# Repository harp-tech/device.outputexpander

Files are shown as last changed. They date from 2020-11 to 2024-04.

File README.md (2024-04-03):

## Harp Output Expander
Harp board to expand the outputs of the current harp ecosystem.

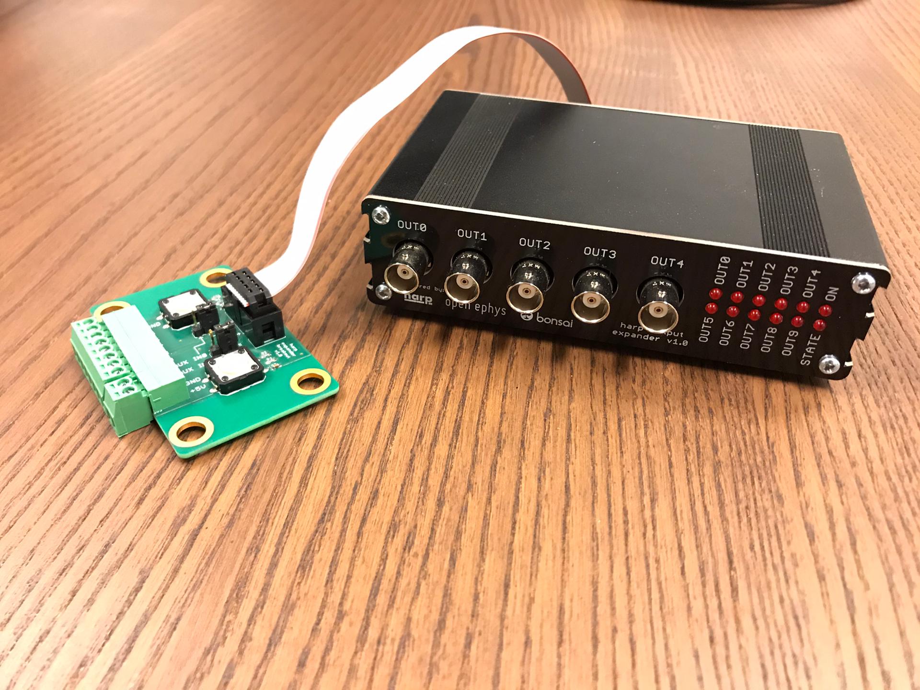
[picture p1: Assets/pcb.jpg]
HarpExpander


### Key Features ###

* TBA

### Connectivity ###

* TBA

## Interface ##

The interface with the Harp Output Expander can be done through [Bonsai](https://bonsai-rx.org/).

## Licensing ##

Each subdirectory will contain a license or, possibly, a set of licenses if it involves both hardware and software.

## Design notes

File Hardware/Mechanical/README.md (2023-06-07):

# Harp Expander Panels

## Licensing

The designs, documentation, and photos available in this repository are free: you can redistribute it and/or modify it under the terms of the used license.
Check file named LICENSE.

Copyright Filipe Carvalho 2020-2023

<br />This work is licensed under a <a rel="license" href="http://creativecommons.org/licenses/by-nc-sa/3.0/igo/">Creative Commons Attribution-NonCommercial-ShareAlike 3.0 IGO License</a>.

If your are interested in obtaining a license to sell this device, please contact info@oeps.tech

[1]: https://docs.google.com/spreadsheets/d/1aobmmEzBDethzIlrm1eg0eYkBqlyX3s9WbA9KgRwVQI/edit?usp=sharing

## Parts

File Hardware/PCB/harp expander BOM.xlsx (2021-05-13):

Qty | Value | Package | Parts | MPN | Type
PCB COMPONENTS
5 | BNC plug |  | BNC0, BNC1, BNC2, BNC3, BNC4 | 73100-0105 | TH
27 | 100nF | C0402 | C1, C3, C5, C7, C9, C12, C13, C14, C15, C16, C17, C18, C19, C20, C21, C22, C25, C26, C27, C28, C29, C30, C31, C32, C35, C36, C40 | MC0402B104K160CT | SMD
9 | 4.7uF | C0603 | C10, C11, C23, C24, C33, C34, C37, C38, C52 | C1608X6S1C475K080AC | SMD
1 | 4.7nF | C0402 | C2 | 885012205084 | SMD
1 | 100u 25V | TT2D6 | C39 | EEUFM1E101B | TH
2 | 47pF | C0402 | C4, C6 | 04025A470JAT2A | SMD
11 | 330pF | C0402 | C41, C42, C43, C44, C45, C46, C47, C48, C49, C50, C51 | C0402C331J5GACTU | SMD
2 | CLCK_JACK | 35RASMT2BHNTRX | CLKIN, CLKOUT | 35RASMT2BHNTRX | SMD
1 | XMEGA-A1TQFP | TQFP100 | IC1 | ATXMEGA128A1U-AU | SMD
1 | USBLC6-2SC6 | SOT23-6L | IC2 | USBLC6-2SC6 | SMD
1 | FT232RL | SSOP28 | IC3 | FT232RL-REEL | SMD
2 | TLV70033DDCR | TSOT23-5 | IC4, IC5 | TLV70033DDCR | SMD
1 | SI8610BC-B-IS | SO-08 | IC6 | SI8610EC-B-IS | SMD
4 | SN74LVC1G125DBVT | SOT23-5 | IC7, IC8, IC9, IC10 | SN74LVC1G125DBVT | SMD
1 | 40R@100MHz | R0805 | L1 | MI0805K400R-10 | SMD
6 | RED_LEDs | 569-011X-X00_LED_ARRAY | LED0, LED1, LED2, LED3, LED4, LED5 | 5690-111-100F | TH
1 | Oscillator | OSCILLATOR_3.2X2.5 | OSC | O 32,0-JT32C-A-K-3,3-LF | SMD | Alternative: DSC1001CI5-032.0000T
1 | PROG HEADER | MA03-2 | PDI | 67996-206HLF | TH
1 | 10R | R0402 | R2 | CRCW040210R0FKEDHP | SMD
12 | 1k | R0402 | R20, R21, R22, R23, R24, R25, R26, R27, R28, R29, R30, R31 | CRCW04021K00FKED | SMD
31 | 10k | R0402 | R3, R9, R10, R11, R12, R13, R14, R15, R16, R17, R19, R38, R43, R46, R47, R53, R54, R55, R56, R57, R58, R59, R60, R61, R62, R63, R64, R65, R66, R67, R68 | CRCW040210K0FKED | SMD
12 | 330R | R0402 | R32, R33, R34, R35, R36, R37, R39, R40, R41, R42, R44, R45 | RC0402FR-07330RL | SMD
11 | 100R | R0603 | R4, R5, R6, R7, R8, R48, R49, R50, R51, R52, R69 | CRCW0603100RFKEAHP | SMD
1 | I/O Header | ML10L | SV1 | SBH11-PBPC-D05-RA-BK | TH
12 | BC850 | SOT23 | T2, T3, T4, T5, T6, T7, T8, T9, T10, T11, T12, T13 | BC850C,215 | SMD
2 | 744245X | SO24L | U1, U2 | 74LVC4245AD,118 | SMD
1 | 74HCT125SO14 | SO14 | U3 | 74HCT125D,653 | SMD
1 | mini USB | 240-0002-1 | USB | UX60-MB-5S8 | SMD
1 |  |  | PCB
POST-PRODUCTION
1 |  |  | Front Panel PCB | PCBWAY
1 |  |  | Rear Panel PCB | PCBWAY
1 |  |  | Enclosure | B5-080BK
4 |  |  | Bumper Cylindrical Dome 9.53mm | SJ-5306-CLEAR-3000/CASE
ACCESSORIES
1 |  |  | 3.5mm stereo jack cable 1.2 m, Black | AV13646
1 |  |  | 0.9 left angle USB cable | USB2HABM3RA
NOTES
 |  |  |  | Number of unique parts | 28
 |  |  |  | Number of unique SMD parts | 23
 |  |  |  | Number of unique TH parts | 5
 |  |  |  | Number of SMD parts | 147
 |  |  |  | Number of TH parts | 14
 |  | Optional
 |  | Holder: MF80BK2

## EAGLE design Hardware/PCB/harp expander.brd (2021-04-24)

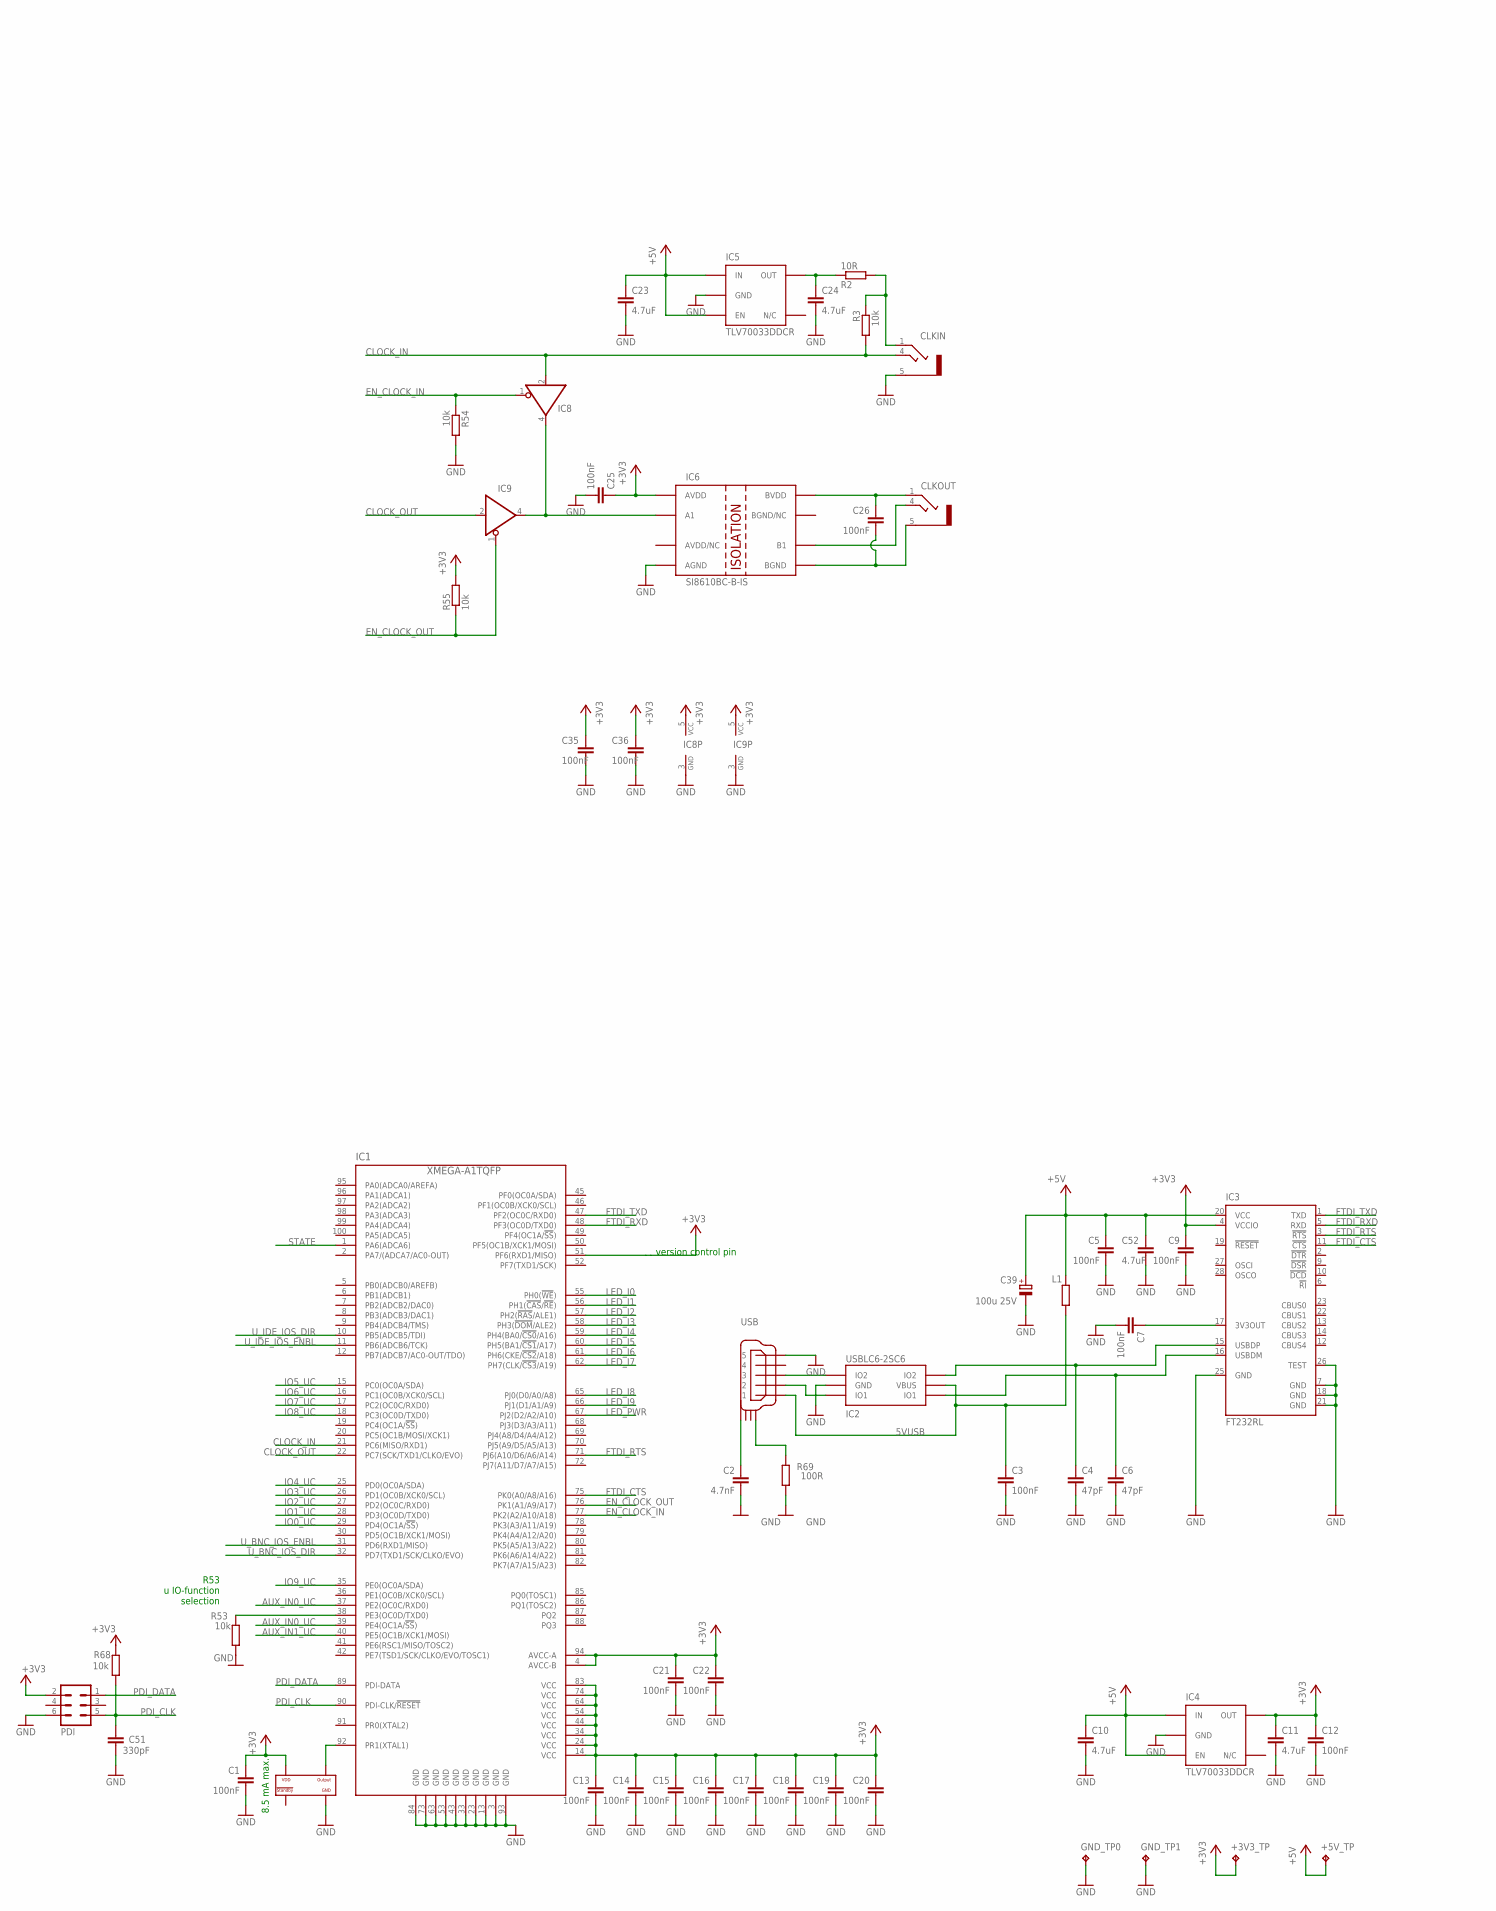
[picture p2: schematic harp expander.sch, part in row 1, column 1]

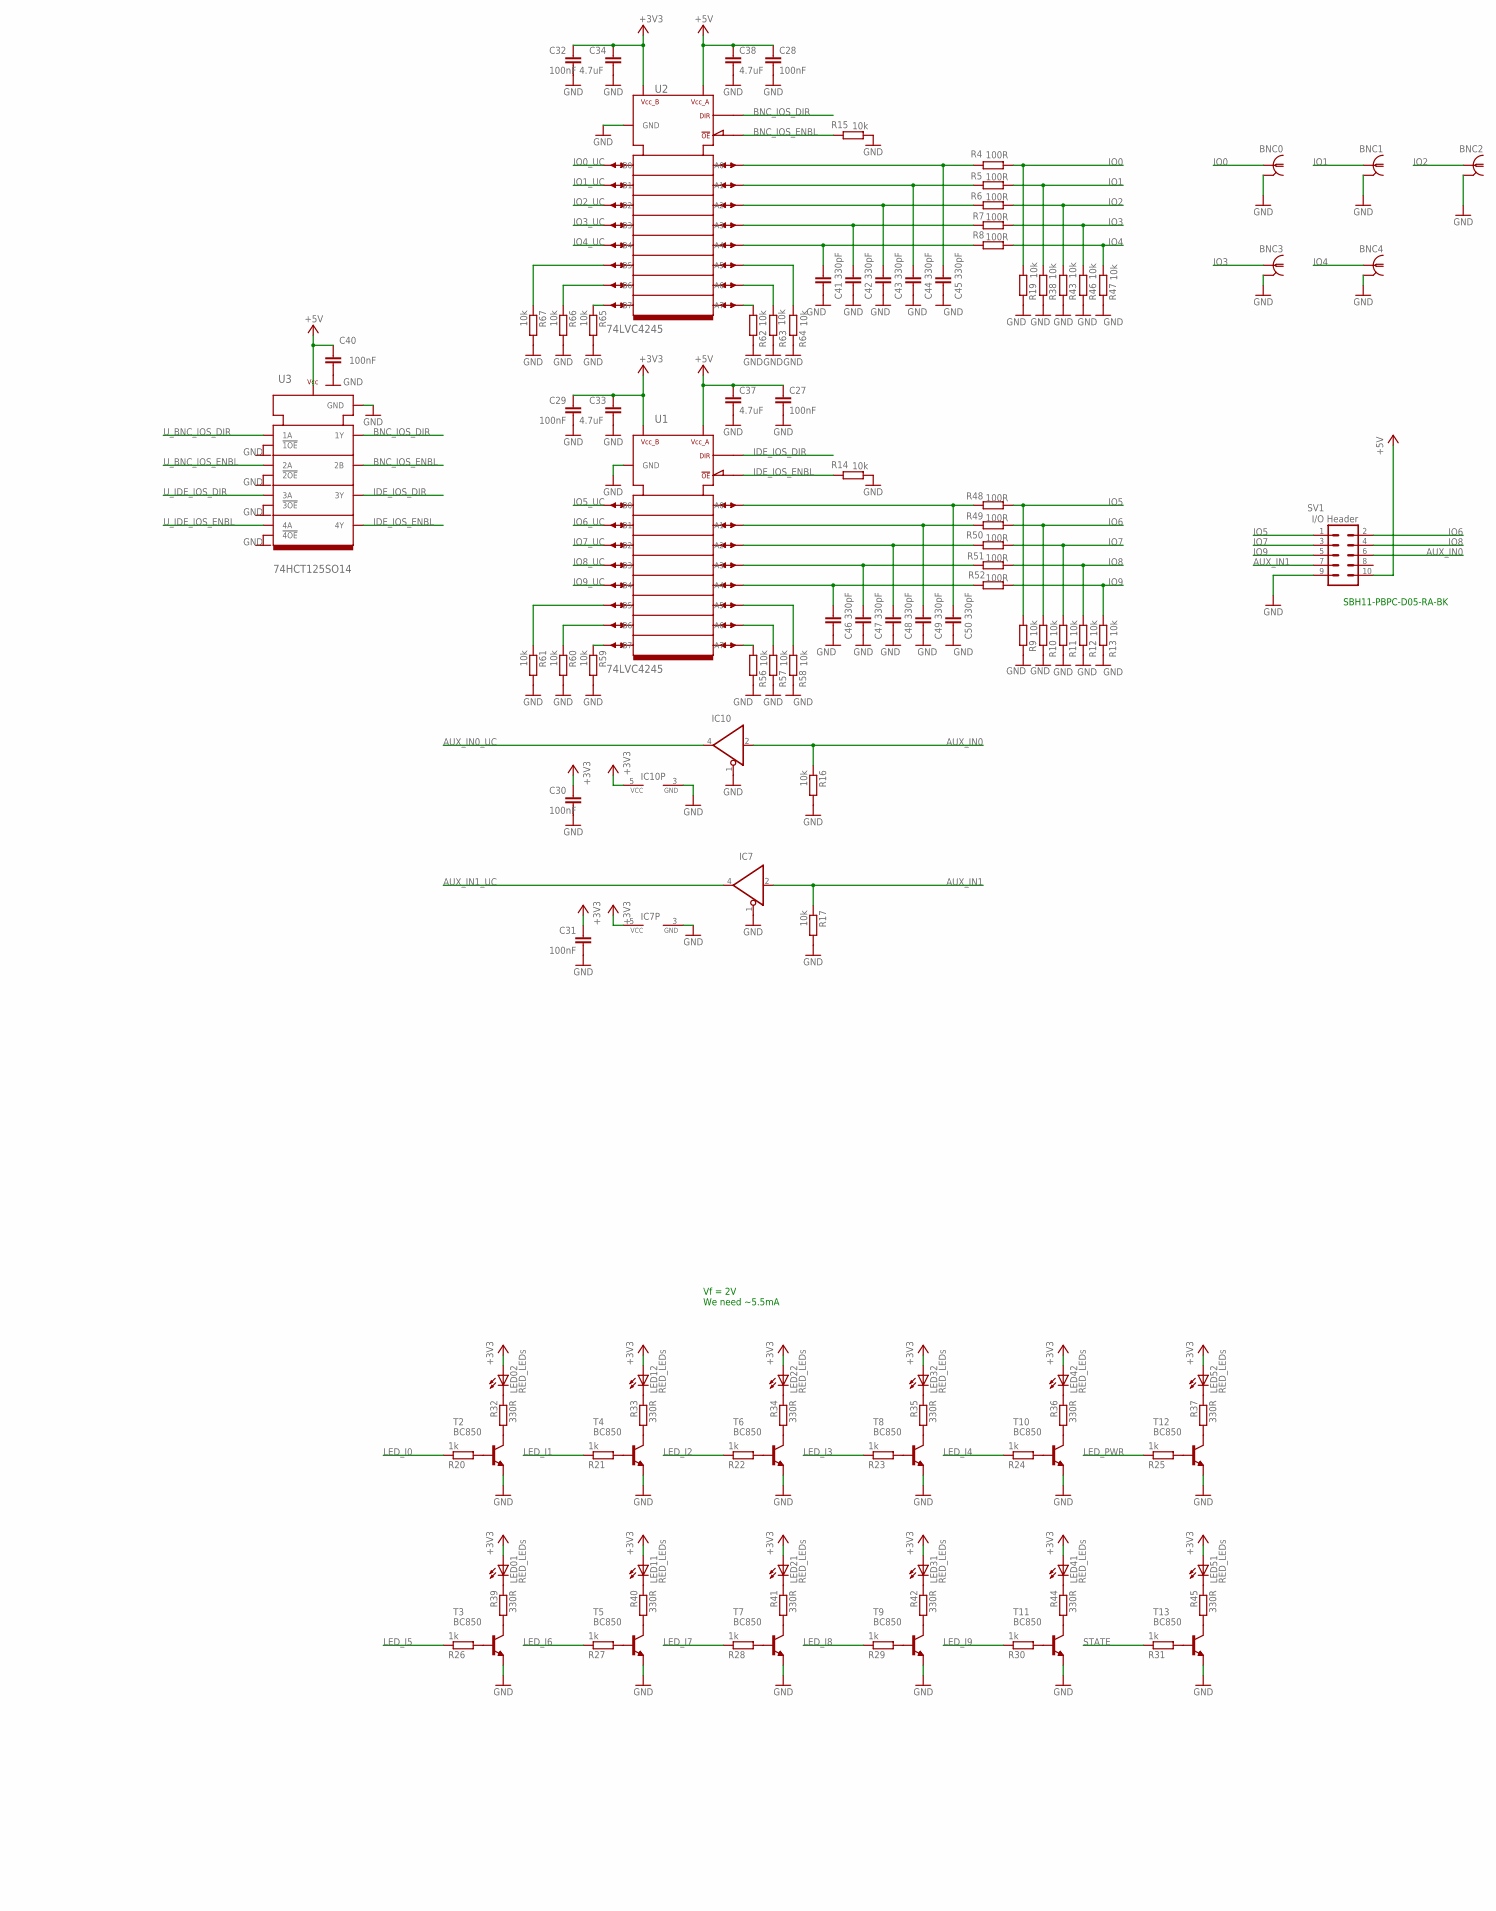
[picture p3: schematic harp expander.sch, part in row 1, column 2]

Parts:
+3V3_TP, +5V_TP: TPPAD1-13; P1-13; MPN n.a.
BNC0, BNC1, BNC2, BNC3, BNC4: BNC plug; 0731000105; MPN 73100-0105
C1, C3, C5, C7, C9, C12, C13, C14, C15, C16, C17, C18, C19, C20, C21, C22, C25, C26, C27, C28, C29, C30, C31, C32, C35, C36, C40: 100nF; C0402; MPN MC0402B104K160CT
C2: 4.7nF; C0402; MPN 885012205084
C4, C6: 47pF; C0402; MPN 04025A470JAT2A
C10, C11, C23, C24, C33, C34, C37, C38, C52: 4.7uF; C0603; MPN C1608X6S1C475K080AC
C39: 100u 25V; TT2D6; MPN EEUFM1E101B
C41, C42, C43, C44, C45, C46, C47, C48, C49, C50, C51: 330pF; C0402; MPN C0402C331J5GACTU
CLKIN: CLCK_JACK; 35RASMT2BHNTRX; MPN 35RASMT2BHNTRX
CLKOUT: CLCK_JACK; 35RASMT2BHNTRX; MPN 35RASMT2BHNTRX
GND_TP0, GND_TP1: TPPAD1-13; P1-13; MPN n.a.
IC1: XMEGA-A1TQFP; TQFP100; MPN ATXMEGA128A1U-AU
IC2: USBLC6-2SC6; SOT23-6L; MPN USBLC6-2SC6
IC3: FT232RL; SSOP28; MPN FT232RL-REEL
IC4, IC5: TLV70033DDCR; TSOT23-5; MPN TLV70033DDCR
IC6: SI8610BC-B-IS; SO-08; MPN SI8610EC-B-IS
IC7, IC8, IC9, IC10: SN74LVC1G125DBVT; SOT23-5; MPN SN74LVC1G125DBVT
L1: 40R@100MHz; R0805; MPN MI0805K400R-10
LED0, LED1, LED2, LED3, LED4, LED5: RED_LEDs; 569-011X-X00_LED_ARRAY; MPN 5690-111-100F
OSC: Oscillator; OSCILLATOR_3.2X2.5; MPN O 32,0-JT32C-A-K-3,3-LF
PDI: PROG HEADER; MA03-2; MPN 67996-206HLF
R2: 10R; R0402; MPN CRCW040210R0FKEDHP
R3, R9, R10, R11, R12, R13, R14, R15, R16, R17, R19, R38, R43, R46, R47, R53, R54, R55, R56, R57, R58, R59, R60, R61, R62, R63, R64, R65, R66, R67, R68: 10k; R0402; MPN CRCW040210K0FKED
R4, R5, R6, R7, R8, R48, R49, R50, R51, R52, R69: 100R; R0603; MPN CRCW0603100RFKEAHP
R20, R21, R22, R23, R24, R25, R26, R27, R28, R29, R30, R31: 1k; R0402; MPN CRCW04021K00FKED
R32, R33, R34, R35, R36, R37, R39, R40, R41, R42, R44, R45: 330R; R0402; MPN RC0402FR-07330RL
SV1: I/O Header; ML10L; MPN SBH11-PBPC-D05-RA-BK
T2, T3, T4, T5, T6, T7, T8, T9, T10, T11, T12, T13: BC850; SOT23; MPN BC850C,215
U1, U2: 744245X; SO24L; MPN 74LVC4245AD,118
U3: 74HCT125SO14; SO14; MPN 74HCT125D,653
USB: mini USB; 240-0002-1; MPN UX60-MB-5S8

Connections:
5VUSB: C3.1, IC2.P$5 (VBUS), L1.2, USB.P$1 (1)
+3V3: +3V3_TP.TP, C1.1, C9.1, C11.1, C12.1, C13.1, C14.1, C15.1, C16.1, C17.1, C18.1, C19.1, C20.1, C21.1, C22.1, C25.1, C29.1, C30.1, C31.1, C32.1, C33.1, C34.1, C35.1, C36.1, IC1.4 (AVCC-B), IC1.14 (VCC), IC1.24 (VCC), IC1.34 (VCC), IC1.44 (VCC), IC1.51 (PF6(RXD1/MISO)), IC1.54 (VCC), IC1.64 (VCC), IC1.74 (VCC), IC1.83 (VCC), IC1.94 (AVCC-A), IC3.4 (VCCIO), IC4.5 (OUT), IC6.1 (AVDD), IC7.5 (VCC), IC8.5 (VCC), IC9.5 (VCC), IC10.5 (VCC), LED0.A1 (A), LED0.A2 (A), LED1.A1 (A), LED1.A2 (A), LED2.A1 (A), LED2.A2 (A), LED3.A1 (A), LED3.A2 (A), LED4.A1 (A), LED4.A2 (A), LED5.A1 (A), LED5.A2 (A), OSC.P$4 (VDD), PDI.2, R55.2, R68.2, U1.23 (VCC_B), U1.24 (VCC_B), U2.23 (VCC_B), U2.24 (VCC_B)
+5V: +5V_TP.TP, C5.1, C10.1, C23.1, C27.1, C28.1, C37.1, C38.1, C39.+, C40.1, C52.1, IC3.20 (VCC), IC4.1 (IN), IC4.3 (EN), IC5.1 (IN), IC5.3 (EN), L1.1, SV1.10, U1.1 (VCC_A), U2.1 (VCC_A), U3.14 (VCC)
AUX_IN0: IC10.2 (I), R16.1, SV1.6
AUX_IN0_UC: IC1.37 (PE2(OC0C/RXD0)), IC1.39 (PE4(OC1A/!SS!)), IC10.4 (O)
AUX_IN1: IC7.2 (I), R17.1, SV1.7
AUX_IN1_UC: IC1.40 (PE5(OC1B/XCK1/MOSI)), IC7.4 (O)
BNC_IOS_DIR: U2.2 (DIR), U3.3 (1Y)
BNC_IOS_ENBL: R15.2, U2.22 (OE), U3.6 (2B)
CLOCK_IN: CLKIN.4, IC1.21 (PC6(MISO/RXD1)), IC8.2 (I), R3.2
CLOCK_OUT: IC1.22 (PC7(SCK/TXD1/CLKO/EVO)), IC9.2 (I)
EN_CLOCK_IN: IC1.77 (PK2(A2/A10/A18)), IC8.1 (OE), R54.1
EN_CLOCK_OUT: IC1.76 (PK1(A1/A9/A17)), IC9.1 (OE), R55.1
FTDI_CTS: IC1.75 (PK0(A0/A8/A16)), IC3.11 (!CTS)
FTDI_RTS: IC1.71 (PJ6(A10/D6/A6/A14)), IC3.3 (!RTS)
FTDI_RXD: IC1.48 (PF3(OC0D/TXD0)), IC3.5 (RXD)
FTDI_TXD: IC1.47 (PF2(OC0C/RXD0)), IC3.1 (TXD)
GND: BNC0.2, BNC0.3 (2), BNC1.2, BNC1.3 (2), BNC2.2, BNC2.3 (2), BNC3.2, BNC3.3 (2), BNC4.2, BNC4.3 (2), C1.2, C2.2, C3.2, C4.2, C5.2, C6.2, C7.2, C9.2, C10.2, C11.2, C12.2, C13.2, C14.2, C15.2, C16.2, C17.2, C18.2, C19.2, C20.2, C21.2, C22.2, C23.2, C24.2, C25.2, C27.2, C28.2, C29.2, C30.2, C31.2, C32.2, C33.2, C34.2, C35.2, C36.2, C37.2, C38.2, C39.-, C40.2, C41.2, C42.2, C43.2, C44.2, C45.2, C46.2, C47.2, C48.2, C49.2, C50.2, C51.2, C52.2, CLKIN.5, GND_TP0.TP, GND_TP1.TP, IC1.3 (GND), IC1.13 (GND), IC1.23 (GND), IC1.33 (GND), IC1.43 (GND), IC1.53 (GND), IC1.63 (GND), IC1.73 (GND), IC1.84 (GND), IC1.93 (GND), IC2.P$2 (GND), IC3.7 (GND), IC3.18 (GND), IC3.21 (GND), IC3.25 (GND), IC3.26 (TEST), IC4.2 (GND), IC5.2 (GND), IC6.4 (AGND), IC7.1 (OE), IC7.3 (GND), IC8.3 (GND), IC9.3 (GND), IC10.1 (OE), IC10.3 (GND), OSC.P$2 (GND), PDI.6, R9.2, R10.2, R11.2, R12.2, R13.2, R14.1, R15.1, R16.2, R17.2, R19.1, R38.1, R43.1, R46.1, R47.1, R53.2, R54.2, R56.2, R57.2, R58.2, R59.2, R60.2, R61.2, R62.2, R63.2, R64.2, R65.2, R66.2, R67.2, R69.2, SV1.9, T2.2 (E), T3.2 (E), T4.2 (E), T5.2 (E), T6.2 (E), T7.2 (E), T8.2 (E), T9.2 (E), T10.2 (E), T11.2 (E), T12.2 (E), T13.2 (E), U1.11 (GND), U1.12 (GND), U1.13 (GND), U2.11 (GND), U2.12 (GND), U2.13 (GND), U3.1 (!1OE), U3.4 (!2OE), U3.7 (GND), U3.10 (!3OE), U3.13 (!4OE), USB.P$5 (5)
GND_ISO: C26.2, CLKOUT.5, IC6.5 (BGND)
IDE_IOS_DIR: U1.2 (DIR), U3.8 (3Y)
IDE_IOS_ENBL: R14.2, U1.22 (OE), U3.11 (4Y)
IO0: BNC0.1, R4.1, R19.2
IO0_UC: IC1.29 (PD4(OC1A/!SS!)), U2.21 (B0)
IO1: BNC1.1, R5.1, R38.2
IO1_UC: IC1.28 (PD3(OC0D/TXD0)), U2.20 (B1)
IO2: BNC2.1, R6.1, R43.2
IO2_UC: IC1.27 (PD2(OC0C/RXD0)), U2.19 (B2)
IO3: BNC3.1, R7.1, R46.2
IO3_UC: IC1.26 (PD1(OC0B/XCK0/SCL)), U2.18 (B3)
IO4: BNC4.1, R8.1, R47.2
IO4_UC: IC1.25 (PD0(OC0A/SDA)), U2.17 (B4)
IO5: R9.1, R48.1, SV1.1
IO5_UC: IC1.15 (PC0(OC0A/SDA)), U1.21 (B0)
IO6: R10.1, R49.1, SV1.2
IO6_UC: IC1.16 (PC1(OC0B/XCK0/SCL)), U1.20 (B1)
IO7: R11.1, R50.1, SV1.3
IO7_UC: IC1.17 (PC2(OC0C/RXD0)), U1.19 (B2)
IO8: R12.1, R51.1, SV1.4
IO8_UC: IC1.18 (PC3(OC0D/TXD0)), U1.18 (B3)
IO9: R13.1, R52.1, SV1.5
IO9_UC: IC1.35 (PE0(OC0A/SDA)), U1.17 (B4)
LED_I0: IC1.55 (PH0(!WE!)), R20.1
LED_I1: IC1.56 (PH1(!CAS!/!RE!)), R21.1
LED_I2: IC1.57 (PH2(!RAS!/ALE1)), R22.1
LED_I3: IC1.58 (PH3(!DOM!/ALE2)), R23.1
LED_I4: IC1.59 (PH4(BA0/!CS0!/A16)), R24.1
LED_I5: IC1.60 (PH5(BA1/!CS1!/A17)), R26.1
LED_I6: IC1.61 (PH6(CKE/!CS2!/A18)), R27.1
LED_I7: IC1.62 (PH7(CLK/!CS3!/A19)), R28.1
LED_I8: IC1.65 (PJ0(D0/A0/A8)), R29.1
LED_I9: IC1.66 (PJ1(D1/A1/A9)), R30.1
LED_PWR: IC1.67 (PJ2(D2/A2/A10)), R25.1
unnamed: R24.2, T10.1 (B)
unnamed: CLKOUT.4, IC6.6 (B1)
unnamed: R20.2, T2.1 (B)
unnamed: LED0.C2 (C), R32.1
unnamed: C26.1, CLKOUT.1, IC6.8 (BVDD)
unnamed: C50.1, R48.2, U1.3 (A0)
unnamed: R36.2, T10.3 (C)
unnamed: R32.2, T2.3 (C)
unnamed: IC1.38 (PE3(OC0D/TXD0)), R53.1
unnamed: R26.2, T3.1 (B)
unnamed: R22.2, T6.1 (B)
unnamed: R39.2, T3.3 (C)
unnamed: R21.2, T4.1 (B)
unnamed: LED3.C1 (C), R42.1
unnamed: R33.2, T4.3 (C)
unnamed: R27.2, T5.1 (B)
unnamed: R34.2, T6.3 (C)
unnamed: R40.2, T5.3 (C)
unnamed: LED3.C2 (C), R35.1
unnamed: R28.2, T7.1 (B)
unnamed: R41.2, T7.3 (C)
unnamed: R23.2, T8.1 (B)
unnamed: R35.2, T8.3 (C)
unnamed: R29.2, T9.1 (B)
unnamed: R42.2, T9.3 (C)
unnamed: LED1.C2 (C), R33.1
unnamed: LED2.C2 (C), R34.1
unnamed: LED1.C1 (C), R40.1
unnamed: LED2.C1 (C), R41.1
unnamed: R30.2, T11.1 (B)
unnamed: LED0.C1 (C), R39.1
unnamed: C7.1, IC3.17 (3V3OUT)
unnamed: IC2.P$1 (IO1), USB.P$2 (2)
unnamed: CLKIN.1, R2.2, R3.1
unnamed: C24.1, IC5.5 (OUT), R2.1
unnamed: IC6.2 (A1), IC8.4 (O), IC9.4 (O)
unnamed: R44.2, T11.3 (C)
unnamed: IC2.P$3 (IO2), USB.P$3 (3)
unnamed: R25.2, T12.1 (B)
unnamed: R37.2, T12.3 (C)
unnamed: R31.2, T13.1 (B)
unnamed: C2.1, USB.SHIELD_4
unnamed: R45.2, T13.3 (C)
unnamed: R69.1, USB.SHIELD_1
unnamed: LED5.C1 (C), R45.1
unnamed: LED5.C2 (C), R37.1
unnamed: LED4.C2 (C), R36.1
unnamed: LED4.C1 (C), R44.1
unnamed: C49.1, R49.2, U1.4 (A1)
unnamed: C48.1, R50.2, U1.5 (A2)
unnamed: C47.1, R51.2, U1.6 (A3)
unnamed: C46.1, R52.2, U1.7 (A4)
unnamed: C45.1, R4.2, U2.3 (A0)
unnamed: C44.1, R5.2, U2.4 (A1)
unnamed: C43.1, R6.2, U2.5 (A2)
unnamed: R61.1, U1.16 (B5)
unnamed: C42.1, R7.2, U2.6 (A3)
unnamed: R60.1, U1.15 (B6)
unnamed: R59.1, U1.14 (B7)
unnamed: R56.1, U1.10 (A7)
unnamed: C41.1, R8.2, U2.7 (A4)
unnamed: R57.1, U1.9 (A6)
unnamed: R58.1, U1.8 (A5)
unnamed: R62.1, U2.10 (A7)
unnamed: R63.1, U2.9 (A6)
unnamed: R64.1, U2.8 (A5)
unnamed: R67.1, U2.16 (B5)
unnamed: R66.1, U2.15 (B6)
unnamed: R65.1, U2.14 (B7)
OSC1: IC1.92 (PR1(XTAL1)), OSC.P$3 (OUTPUT)
PDI_CLK: C51.1, IC1.90 (PDI-CLK/!RESET), PDI.5, R68.1
PDI_DATA: IC1.89 (PDI-DATA), PDI.1
STATE: IC1.1 (PA6(ADCA6)), R31.1
USBDM: C6.1, IC2.P$6 (IO1), IC3.16 (USBDM)
USBDP: C4.1, IC2.P$4 (IO2), IC3.15 (USBDP)
U_BNC_IOS_DIR: IC1.32 (PD7(TXD1/SCK/CLKO/EVO)), U3.2 (1A)
U_BNC_IOS_ENBL: IC1.31 (PD6(RXD1/MISO)), U3.5 (2A)
U_IDE_IOS_DIR: IC1.10 (PB5(ADCB5/TDI)), U3.9 (3A)
U_IDE_IOS_ENBL: IC1.11 (PB6(ADCB6/TCK)), U3.12 (4A)

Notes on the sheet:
Vf = 2V We need ~5.5mA
8.5 mA max.
SBH11-PBPC-D05-RA-BK
R53 u IO-function selection
version control pin

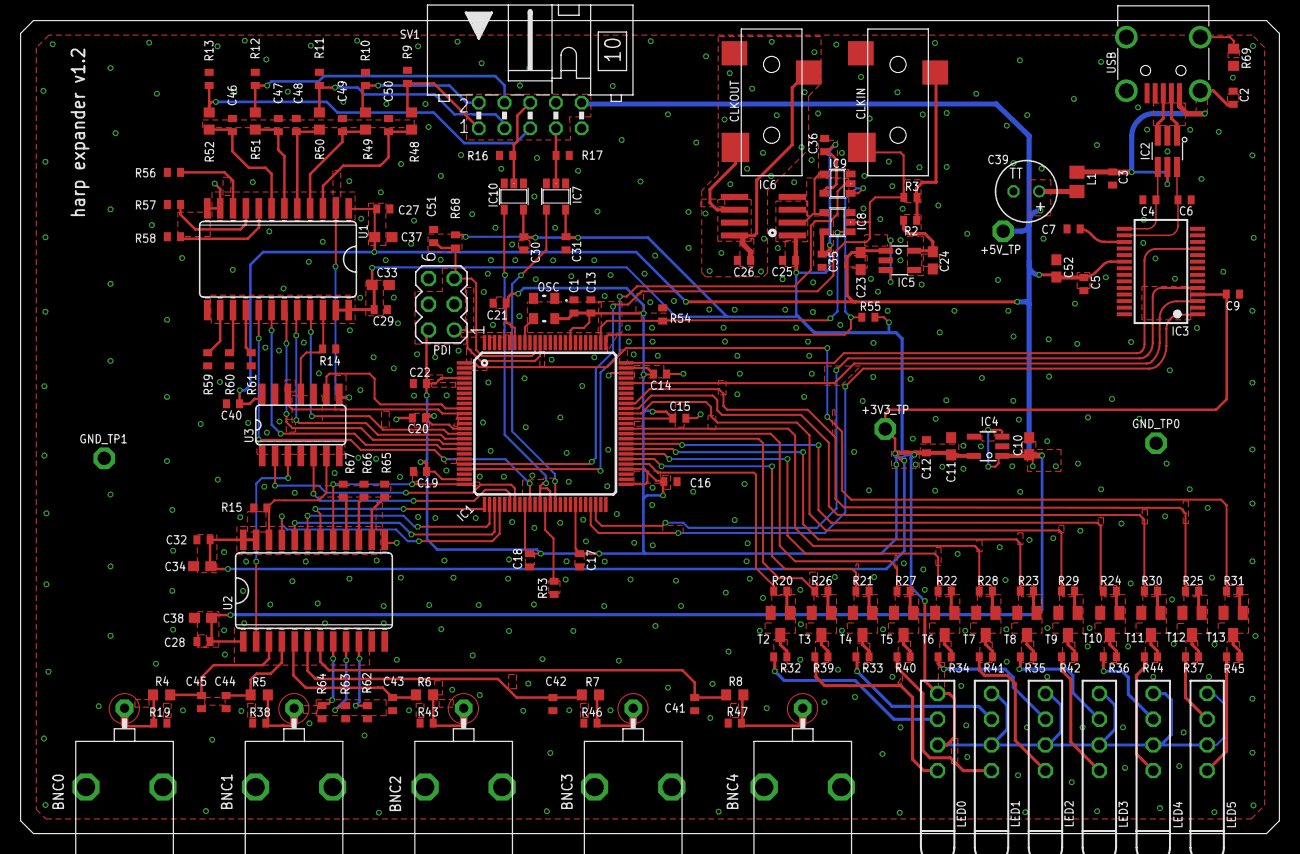
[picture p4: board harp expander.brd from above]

Board: 2 copper layers, 124.5 x 80.4 mm, 165 parts (0 on the bottom side), 131 nets.

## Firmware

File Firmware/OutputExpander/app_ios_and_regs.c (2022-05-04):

#include <avr/io.h>
#include "hwbp_core_types.h"
#include "app_ios_and_regs.h"

/************************************************************************/
/* Configure and initialize IOs                                         */
/************************************************************************/
void init_ios(void)
{	/* Configure input pins */
	io_pin2in(&PORTE, 2, PULL_IO_TRISTATE, SENSE_IO_EDGES_BOTH);         // AUX_INPUT0
	io_pin2in(&PORTE, 5, PULL_IO_TRISTATE, SENSE_IO_EDGES_BOTH);         // AUX_INPUT1
	io_pin2in(&PORTE, 3, PULL_IO_UP, SENSE_IO_EDGES_BOTH);               // IS_OUTPUT
	io_pin2in(&PORTA, 0, PULL_IO_DOWN, SENSE_IO_EDGES_BOTH);             // PA0
	io_pin2in(&PORTA, 1, PULL_IO_DOWN, SENSE_IO_EDGES_BOTH);             // PA1
	io_pin2in(&PORTA, 2, PULL_IO_DOWN, SENSE_IO_EDGES_BOTH);             // PA2
	io_pin2in(&PORTA, 3, PULL_IO_DOWN, SENSE_IO_EDGES_BOTH);             // PA3
	io_pin2in(&PORTA, 4, PULL_IO_DOWN, SENSE_IO_EDGES_BOTH);             // PA4
	io_pin2in(&PORTA, 5, PULL_IO_DOWN, SENSE_IO_EDGES_BOTH);             // PA5
	io_pin2in(&PORTA, 7, PULL_IO_DOWN, SENSE_IO_EDGES_BOTH);             // PA7
	io_pin2in(&PORTB, 0, PULL_IO_DOWN, SENSE_IO_EDGES_BOTH);             // PB0
	io_pin2in(&PORTB, 1, PULL_IO_DOWN, SENSE_IO_EDGES_BOTH);             // PB1
	io_pin2in(&PORTB, 2, PULL_IO_DOWN, SENSE_IO_EDGES_BOTH);             // PB2
	io_pin2in(&PORTB, 3, PULL_IO_DOWN, SENSE_IO_EDGES_BOTH);             // PB3
	io_pin2in(&PORTB, 4, PULL_IO_DOWN, SENSE_IO_EDGES_BOTH);             // PB4
	io_pin2in(&PORTB, 7, PULL_IO_DOWN, SENSE_IO_EDGES_BOTH);             // PB7
	io_pin2in(&PORTC, 4, PULL_IO_DOWN, SENSE_IO_EDGES_BOTH);             // PC4
	io_pin2in(&PORTC, 5, PULL_IO_DOWN, SENSE_IO_EDGES_BOTH);             // PC5
	io_pin2in(&PORTD, 5, PULL_IO_DOWN, SENSE_IO_EDGES_BOTH);             // PD5
	io_pin2in(&PORTE, 1, PULL_IO_DOWN, SENSE_IO_EDGES_BOTH);             // PE1
	io_pin2in(&PORTE, 6, PULL_IO_DOWN, SENSE_IO_EDGES_BOTH);             // PE6
	io_pin2in(&PORTE, 7, PULL_IO_DOWN, SENSE_IO_EDGES_BOTH);             // PE7
	io_pin2in(&PORTF, 0, PULL_IO_DOWN, SENSE_IO_EDGES_BOTH);             // PF0
	io_pin2in(&PORTF, 1, PULL_IO_DOWN, SENSE_IO_EDGES_BOTH);             // PF1
	io_pin2in(&PORTF, 4, PULL_IO_DOWN, SENSE_IO_EDGES_BOTH);             // PF4
	io_pin2in(&PORTF, 5, PULL_IO_DOWN, SENSE_IO_EDGES_BOTH);             // PF5
	io_pin2in(&PORTF, 6, PULL_IO_DOWN, SENSE_IO_EDGES_BOTH);             // PF6
	io_pin2in(&PORTF, 7, PULL_IO_DOWN, SENSE_IO_EDGES_BOTH);             // PF7
	io_pin2in(&PORTJ, 3, PULL_IO_DOWN, SENSE_IO_EDGES_BOTH);             // PJ3
	io_pin2in(&PORTJ, 4, PULL_IO_DOWN, SENSE_IO_EDGES_BOTH);             // PJ4
	io_pin2in(&PORTJ, 5, PULL_IO_DOWN, SENSE_IO_EDGES_BOTH);             // PJ5
	io_pin2in(&PORTJ, 7, PULL_IO_DOWN, SENSE_IO_EDGES_BOTH);             // PJ7
	io_pin2in(&PORTK, 3, PULL_IO_DOWN, SENSE_IO_EDGES_BOTH);             // PK3
	io_pin2in(&PORTK, 4, PULL_IO_DOWN, SENSE_IO_EDGES_BOTH);             // PK4
	io_pin2in(&PORTK, 5, PULL_IO_DOWN, SENSE_IO_EDGES_BOTH);             // PK5
	io_pin2in(&PORTK, 6, PULL_IO_DOWN, SENSE_IO_EDGES_BOTH);             // PK6
	io_pin2in(&PORTK, 7, PULL_IO_DOWN, SENSE_IO_EDGES_BOTH);             // PK7
	io_pin2in(&PORTQ, 0, PULL_IO_DOWN, SENSE_IO_EDGES_BOTH);             // PQ0
	io_pin2in(&PORTQ, 1, PULL_IO_DOWN, SENSE_IO_EDGES_BOTH);             // PQ1
	io_pin2in(&PORTQ, 2, PULL_IO_DOWN, SENSE_IO_EDGES_BOTH);             // PQ2
	io_pin2in(&PORTQ, 3, PULL_IO_DOWN, SENSE_IO_EDGES_BOTH);             // PQ3

	/* Configure input interrupts */
	io_set_int(&PORTE, INT_LEVEL_LOW, 0, (1<<2), false);                 // AUX_INPUT0
	io_set_int(&PORTE, INT_LEVEL_LOW, 0, (1<<5), false);                 // AUX_INPUT1

	/* Configure output pins */
	io_pin2out(&PORTH, 0, OUT_IO_DIGITAL, IN_EN_IO_EN);                  // LED_0
	io_pin2out(&PORTH, 1, OUT_IO_DIGITAL, IN_EN_IO_EN);                  // LED_1
	io_pin2out(&PORTH, 2, OUT_IO_DIGITAL, IN_EN_IO_EN);                  // LED_2
	io_pin2out(&PORTH, 3, OUT_IO_DIGITAL, IN_EN_IO_EN);                  // LED_3
	io_pin2out(&PORTH, 4, OUT_IO_DIGITAL, IN_EN_IO_EN);                  // LED_4
	io_pin2out(&PORTH, 5, OUT_IO_DIGITAL, IN_EN_IO_EN);                  // LED_5
	io_pin2out(&PORTH, 6, OUT_IO_DIGITAL, IN_EN_IO_EN);                  // LED_6
	io_pin2out(&PORTH, 7, OUT_IO_DIGITAL, IN_EN_IO_EN);                  // LED_7
	io_pin2out(&PORTJ, 0, OUT_IO_DIGITAL, IN_EN_IO_EN);                  // LED_8
	io_pin2out(&PORTJ, 1, OUT_IO_DIGITAL, IN_EN_IO_EN);                  // LED_9
	io_pin2out(&PORTJ, 2, OUT_IO_DIGITAL, IN_EN_IO_EN);                  // LED_PWR
	io_pin2out(&PORTA, 6, OUT_IO_DIGITAL, IN_EN_IO_EN);                  // LED_STATE
	io_pin2out(&PORTB, 5, OUT_IO_DIGITAL, IN_EN_IO_EN);                  // IDE_IOS_DIR
	io_pin2out(&PORTB, 6, OUT_IO_DIGITAL, IN_EN_IO_EN);                  // IDE_IOS_EN
	io_pin2out(&PORTD, 7, OUT_IO_DIGITAL, IN_EN_IO_EN);                  // BNC_IOS_DIR
	io_pin2out(&PORTD, 6, OUT_IO_DIGITAL, IN_EN_IO_EN);                  // BNC_IOS_EN
	io_pin2out(&PORTK, 1, OUT_IO_DIGITAL, IN_EN_IO_EN);                  // EN_CLOCK_OUT
	io_pin2out(&PORTK, 2, OUT_IO_DIGITAL, IN_EN_IO_EN);                  // EN_CLOCK_IN
	io_pin2out(&PORTD, 4, OUT_IO_DIGITAL, IN_EN_IO_EN);                  // OUT0
	io_pin2out(&PORTD, 3, OUT_IO_DIGITAL, IN_EN_IO_EN);                  // OUT1
	io_pin2out(&PORTD, 2, OUT_IO_DIGITAL, IN_EN_IO_EN);                  // OUT2
	io_pin2out(&PORTD, 1, OUT_IO_DIGITAL, IN_EN_IO_EN);                  // OUT3
	io_pin2out(&PORTD, 0, OUT_IO_DIGITAL, IN_EN_IO_EN);                  // OUT4
	io_pin2out(&PORTC, 0, OUT_IO_DIGITAL, IN_EN_IO_EN);                  // OUT5
	io_pin2out(&PORTC, 1, OUT_IO_DIGITAL, IN_EN_IO_EN);                  // OUT6
	io_pin2out(&PORTC, 2, OUT_IO_DIGITAL, IN_EN_IO_EN);                  // OUT7
	io_pin2out(&PORTC, 3, OUT_IO_DIGITAL, IN_EN_IO_EN);                  // OUT8
	io_pin2out(&PORTE, 0, OUT_IO_DIGITAL, IN_EN_IO_EN);                  // OUT9

	/* Initialize output pins */
	clr_LED_0;
	clr_LED_1;
	clr_LED_2;
	clr_LED_3;
	clr_LED_4;
	clr_LED_5;
	clr_LED_6;
	clr_LED_7;
	clr_LED_8;
	clr_LED_9;
	clr_LED_PWR;
	clr_LED_STATE;
	clr_IDE_IOS_DIR;
	clr_IDE_IOS_EN;
	clr_BNC_IOS_DIR;
	clr_BNC_IOS_EN;
	clr_EN_CLOCK_OUT;
	set_EN_CLOCK_IN;
	clr_OUT0;
	clr_OUT1;
	clr_OUT2;
	clr_OUT3;
	clr_OUT4;
	clr_OUT5;
	clr_OUT6;
	clr_OUT7;
	clr_OUT8;
	clr_OUT9;
}

/************************************************************************/
/* Registers' stuff                                                     */
/************************************************************************/
AppRegs app_regs;

uint8_t app_regs_type[] = {
	TYPE_U8,
	TYPE_U8,
	TYPE_U8,
	TYPE_U16,
	TYPE_U16,
	TYPE_U16,
	TYPE_U16,
	TYPE_U16,
	TYPE_U16,
	TYPE_U16,
	TYPE_FLOAT,
	TYPE_FLOAT,
	TYPE_U16,
	TYPE_FLOAT,
	TYPE_FLOAT,
	TYPE_U8,
	TYPE_U8,
	TYPE_U8,
	TYPE_FLOAT,
	TYPE_FLOAT,
	TYPE_U16,
	TYPE_FLOAT,
	TYPE_FLOAT,
	TYPE_U8,
	TYPE_U8,
	TYPE_U8,
	TYPE_FLOAT,
	TYPE_FLOAT,
	TYPE_U16,
	TYPE_FLOAT,
	TYPE_FLOAT,
	TYPE_U8,
	TYPE_U8,
	TYPE_U8,
	TYPE_U8,
	TYPE_U8,
	TYPE_U8,
	TYPE_U16,
	TYPE_U16,
	TYPE_U16,
	TYPE_U8,
	TYPE_U8,
	TYPE_U8,
	TYPE_U8,
	TYPE_U16,
	TYPE_U16,
	TYPE_U16,
	TYPE_U16,
	TYPE_U16,
	TYPE_U16,
	TYPE_U16,
	TYPE_U16,
	TYPE_U16,
	TYPE_U16,
	TYPE_U16,
	TYPE_U8,
	TYPE_U8,
	TYPE_U8,
	TYPE_U16,
	TYPE_U8,
	TYPE_U8,
	TYPE_U8,
	TYPE_U16,
	TYPE_U16,
	TYPE_U16,
	TYPE_U16,
	TYPE_U8,
	TYPE_U8,
	TYPE_I16,
};

uint16_t app_regs_n_elements[] = {
	1,
	1,
	1,
	1,
	1,
	1,
	1,
	1,
	1,
	1,
	1,
	1,
	1,
	1,
	1,
	1,
	1,
	1,
	1,
	1,
	1,
	1,
	1,
	1,
	1,
	1,
	1,
	1,
	1,
	1,
	1,
	1,
	1,
	1,
	1,
	1,
	1,
	1,
	1,
	1,
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
};

uint8_t *app_regs_pointer[] = {
	(uint8_t*)(&app_regs.REG_AUX_INPUTS),
	(uint8_t*)(&app_regs.REG_AUX_INPUTS_RISING_EDGE_ENABLE),
	(uint8_t*)(&app_regs.REG_AUX_INPUTS_FALLING_EDGE_ENABLE),
	(uint8_t*)(&app_regs.REG_OUTPUTS_SET),
	(uint8_t*)(&app_regs.REG_OUTPUTS_CLEAR),
	(uint8_t*)(&app_regs.REG_OUTPUTS_TOGGLE),
	(uint8_t*)(&app_regs.REG_OUTPUTS_WRITE),
	(uint8_t*)(&app_regs.REG_PWM_AND_STIM_ENABLE),
	(uint8_t*)(&app_regs.REG_PWM_AND_STIM_DISABLE),
	(uint8_t*)(&app_regs.REG_PWM_AND_STIM_WRITE),
	(uint8_t*)(&app_regs.REG_PWM0_FREQ),
	(uint8_t*)(&app_regs.REG_PWM0_DUTYCYCLE),
	(uint8_t*)(&app_regs.REG_PWM0_COUNT),
	(uint8_t*)(&app_regs.REG_PWM0_REAL_FREQ),
	(uint8_t*)(&app_regs.REG_PWM0_REAL_DUTYCYCLE),
	(uint8_t*)(&app_regs.REG_PWM0_MODE),
	(uint8_t*)(&app_regs.REG_PWM0_TRIG),
	(uint8_t*)(&app_regs.REG_PWM0_CONF_EVENT),
	(uint8_t*)(&app_regs.REG_PWM1_FREQ),
	(uint8_t*)(&app_regs.REG_PWM1_DUTYCYCLE),
	(uint8_t*)(&app_regs.REG_PWM1_COUNT),
	(uint8_t*)(&app_regs.REG_PWM1_REAL_FREQ),
	(uint8_t*)(&app_regs.REG_PWM1_REAL_DUTYCYCLE),
	(uint8_t*)(&app_regs.REG_PWM1_MODE),
	(uint8_t*)(&app_regs.REG_PWM1_TRIG),
	(uint8_t*)(&app_regs.REG_PWM1_CONF_EVENT),
	(uint8_t*)(&app_regs.REG_PWM2_FREQ),
	(uint8_t*)(&app_regs.REG_PWM2_DUTYCYCLE),
	(uint8_t*)(&app_regs.REG_PWM2_COUNT),
	(uint8_t*)(&app_regs.REG_PWM2_REAL_FREQ),
	(uint8_t*)(&app_regs.REG_PWM2_REAL_DUTYCYCLE),
	(uint8_t*)(&app_regs.REG_PWM2_MODE),
	(uint8_t*)(&app_regs.REG_PWM2_TRIG),
	(uint8_t*)(&app_regs.REG_PWM2_CONF_EVENT),
	(uint8_t*)(&app_regs.REG_PWM_START),
	(uint8_t*)(&app_regs.REG_PWM_STOP),
	(uint8_t*)(&app_regs.REG_PWM_RISE_EVENT),
	(uint8_t*)(&app_regs.REG_STIM0_T_ON),
	(uint8_t*)(&app_regs.REG_STIM0_T_OFF),
	(uint8_t*)(&app_regs.REG_STIM0_COUNT),
	(uint8_t*)(&app_regs.REG_STIM0_MODE),
	(uint8_t*)(&app_regs.REG_STIM0_TRIG),
	(uint8_t*)(&app_regs.REG_STIM_START),
	(uint8_t*)(&app_regs.REG_STIM_STOP),
	(uint8_t*)(&app_regs.REG_PULSE_ENABLE),
	(uint8_t*)(&app_regs.REG_PULSE_OUT0),
	(uint8_t*)(&app_regs.REG_PULSE_OUT1),
	(uint8_t*)(&app_regs.REG_PULSE_OUT2),
	(uint8_t*)(&app_regs.REG_PULSE_OUT3),
	(uint8_t*)(&app_regs.REG_PULSE_OUT4),
	(uint8_t*)(&app_regs.REG_PULSE_OUT5),
	(uint8_t*)(&app_regs.REG_PULSE_OUT6),
	(uint8_t*)(&app_regs.REG_PULSE_OUT7),
	(uint8_t*)(&app_regs.REG_PULSE_OUT8),
	(uint8_t*)(&app_regs.REG_PULSE_OUT9),
	(uint8_t*)(&app_regs.REG_EXPANSION_OPTIONS),
	(uint8_t*)(&app_regs.REG_RESERVED2),
	(uint8_t*)(&app_regs.REG_RESERVED3),
	(uint8_t*)(app_regs.REG_MAG_ENCODER_READ),
	(uint8_t*)(&app_regs.REG_MAG_ENCODER_MODE),
	(uint8_t*)(&app_regs.REG_RESERVED4),
	(uint8_t*)(&app_regs.REG_RESERVED5),
	(uint8_t*)(&app_regs.REG_SERVO_PERIOD_US),
	(uint8_t*)(&app_regs.REG_SERVO0_PULSE_US),
	(uint8_t*)(&app_regs.REG_SERVO1_PULSE_US),
	(uint8_t*)(&app_regs.REG_SERVO2_PULSE_US),
	(uint8_t*)(&app_regs.REG_RESERVED6),
	(uint8_t*)(&app_regs.REG_RESERVED7),
	(uint8_t*)(app_regs.REG_OPTICAL_TRACKING_READ),
};

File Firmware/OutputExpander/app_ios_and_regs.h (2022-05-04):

#ifndef _APP_IOS_AND_REGS_H_
#define _APP_IOS_AND_REGS_H_
#include "cpu.h"

void init_ios(void);
/************************************************************************/
/* Definition of input pins                                             */
/************************************************************************/
// AUX_INPUT0             Description: Auxiliary input 0
// AUX_INPUT1             Description: Auxiliary input 1
// IS_OUTPUT              Description: Check for the right hardware
// PA0                    Description: 
// PA1                    Description: 
// PA2                    Description: 
// PA3                    Description: 
// PA4                    Description: 
// PA5                    Description: 
// PA7                    Description: 
// PB0                    Description: 
// PB1                    Description: 
// PB2                    Description: 
// PB3                    Description: 
// PB4                    Description: 
// PB7                    Description: 
// PC4                    Description: 
// PC5                    Description: 
// PD5                    Description: 
// PE1                    Description: 
// PE6                    Description: 
// PE7                    Description: 
// PF0                    Description: 
// PF1                    Description: 
// PF4                    Description: 
// PF5                    Description: 
// PF6                    Description: 
// PF7                    Description: 
// PJ3                    Description: 
// PJ4                    Description: 
// PJ5                    Description: 
// PJ7                    Description: 
// PK3                    Description: 
// PK4                    Description: 
// PK5                    Description: 
// PK6                    Description: 
// PK7                    Description: 
// PQ0                    Description: 
// PQ1                    Description: 
// PQ2                    Description: 
// PQ3                    Description: 

#define read_AUX_INPUT0 read_io(PORTE, 2)       // AUX_INPUT0
#define read_AUX_INPUT1 read_io(PORTE, 5)       // AUX_INPUT1
#define read_IS_OUTPUT read_io(PORTE, 3)        // IS_OUTPUT
#define read_PA0 read_io(PORTA, 0)              // PA0
#define read_PA1 read_io(PORTA, 1)              // PA1
#define read_PA2 read_io(PORTA, 2)              // PA2
#define read_PA3 read_io(PORTA, 3)              // PA3
#define read_PA4 read_io(PORTA, 4)              // PA4
#define read_PA5 read_io(PORTA, 5)              // PA5
#define read_PA7 read_io(PORTA, 7)              // PA7
#define read_PB0 read_io(PORTB, 0)              // PB0
#define read_PB1 read_io(PORTB, 1)              // PB1
#define read_PB2 read_io(PORTB, 2)              // PB2
#define read_PB3 read_io(PORTB, 3)              // PB3
#define read_PB4 read_io(PORTB, 4)              // PB4
#define read_PB7 read_io(PORTB, 7)              // PB7
#define read_PC4 read_io(PORTC, 4)              // PC4
#define read_PC5 read_io(PORTC, 5)              // PC5
#define read_PD5 read_io(PORTD, 5)              // PD5
#define read_PE1 read_io(PORTE, 1)              // PE1
#define read_PE6 read_io(PORTE, 6)              // PE6
#define read_PE7 read_io(PORTE, 7)              // PE7
#define read_PF0 read_io(PORTF, 0)              // PF0
#define read_PF1 read_io(PORTF, 1)              // PF1
#define read_PF4 read_io(PORTF, 4)              // PF4
#define read_PF5 read_io(PORTF, 5)              // PF5
#define read_PF6 read_io(PORTF, 6)              // PF6
#define read_PF7 read_io(PORTF, 7)              // PF7
#define read_PJ3 read_io(PORTJ, 3)              // PJ3
#define read_PJ4 read_io(PORTJ, 4)              // PJ4
#define read_PJ5 read_io(PORTJ, 5)              // PJ5
#define read_PJ7 read_io(PORTJ, 7)              // PJ7
#define read_PK3 read_io(PORTK, 3)              // PK3
#define read_PK4 read_io(PORTK, 4)              // PK4
#define read_PK5 read_io(PORTK, 5)              // PK5
#define read_PK6 read_io(PORTK, 6)              // PK6
#define read_PK7 read_io(PORTK, 7)              // PK7
#define read_PQ0 read_io(PORTQ, 0)              // PQ0
#define read_PQ1 read_io(PORTQ, 1)              // PQ1
#define read_PQ2 read_io(PORTQ, 2)              // PQ2
#define read_PQ3 read_io(PORTQ, 3)              // PQ3
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

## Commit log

2020-10-31 Added gerbers, centroids and BOM.
    [harp expander BOM.xlsx]
2020-10-31 Added panels and production files.
    [harp expander rear panel.brd, harp output expander front panel.brd]
2020-11-04 Corrected rear panel's silk screen.
    [harp expander rear panel.brd]
2020-11-04 Added panels' gerber files.
    [copper_bottom.gbr, copper_top.gbr, gerber_job.gbrjob, profile.gbr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]
2020-11-15 Minor corrections.
    [harp expander.brd, harp expander.sch]
2020-12-19 Added ability to connect to a Teensy/Arduino and to read rotary encoders.
    [harp expander.brd, harp expander.sch]
2020-12-19 Added ability to be used as a clock generator.
    [harp expander BOM.xlsx, harp expander.brd, harp expander.sch]
2020-12-19 Minor corrections on layout and schematics.
    [harp expander.brd, harp expander.sch]
2020-12-19 Updated BOM.
    [harp expander BOM.xlsx]
2020-12-19 Updated production files.
    [harp expander BOM_simplified.xlsx]
2020-12-20 Minor corrections to BOMs.
    [harp expander BOM.xlsx]
2021-02-06 Updated for the first functional code (some features still to implement).
    [registers_output.xls]
2021-02-06 Implemented LED management.
2021-02-07 Corrected visualization and implemented the magnetic encoder expansion.
    [registers_output.xls]
2021-02-07 Added code to control the expander servo driver.
    [registers_output.xls]
2021-02-11 Changed the audio cable PN.
    [harp expander BOM.xlsx]
2021-02-11 Replaced oscillator with a more precise one.
    [harp expander BOM.xlsx, harp expander BOM_simplified.xlsx]
2021-02-16 Minor corrections to registers' descriptions.
    [registers_output.xls]
2021-02-16 Corrected bad timing when using the servo expander.
2021-02-21 Reversed the hardware's resistor assembly.
2021-02-21 Correct bad servo driver configuration.
2021-02-23 Added default for the magnetic encoder sample rate.
2021-03-04 Add Bonsai interface for harp expander devices
2021-03-07 Implemented ability to filter selected transitions on both auxiliary input lines.
    [registers_output.xls]
2021-03-07 Added new registers to control PWM and stimulation.
    [registers_output.xls]
2021-03-07 increased firmware version to 2.0.
    [registers_output.xls]
2021-03-08 Renamed STIM registers and added PULSE registers.
    [registers_output.xls]
2021-03-08 Implemented the ability to produce up to 3 different PWMs.
    [registers_output.xls]
2021-03-16 Added more flexibility to enable and disable PWM.
    [registers_output.xls]
2021-03-23 Add support for configuring expansion board modes
2021-04-24 Added filtering on inputs and reset lines to prevent erroneous behavior in noisy environments.
    [harp expander BOM.xlsx, harp expander BOM_simplified.xlsx, harp expander.brd, harp expander.sch]
2021-04-24 Added a photo of the assembled device.
2021-04-27 Added ability to read a rotary encoder.
    [registers_output.xls]
2021-05-13 Minor BOM correction.
    [harp expander BOM.xlsx]
2021-11-27 Mapped the clock enables in the IO list.
    [registers_output.xls]
2022-05-04 Implemented the optical tracking reading.
    [registers_output.xls]
2023-03-21 Updated Harp Core to version 1.12.
    [registers_output.xls]
2023-04-03 Updated panels to match PCB version.
    [gerber_job.gbrjob, harp output expander front panel.brd, silkscreen_top.gbr]
2023-04-25 Refactor repo structure to follow latest specs
    [copper_bottom.gbr, copper_top.gbr, gerber_job.gbrjob, harp expander BOM.xlsx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]
2023-04-25 Add first draft of device schema
2023-04-25 Add Device classes
2023-06-02 Update `Device` classes to the new schema
2023-06-07 Update `Device` class
2023-06-15 Add encoder and flow sensor payload metadata
2023-06-15 Rename to sample rate for consistency
2024-11-09 Fix package metadata to embed device metadata
2024-11-16 Favor harp-tech as source of device schema
2025-10-22 Updated firmware version to 2.3 in device.yml
2026-06-29 Moved Eagle to KiCAD:
    [IOs.kicad_sch, LEDs & ClockIO.kicad_sch, core.kicad_sch, harp expander BOM.xlsx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]
2026-06-29 Moved panels from Eagle to KiCAD.
    [IOs.kicad_sch, LEDs & ClockIO.kicad_sch, copper_bottom.gbr, copper_top.gbr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]
2026-06-29 Updated Gerbers.
    [harp output expander front panel-B_Cu.gbr, harp output expander front panel-B_Mask.gbr, harp output expander front panel-B_Paste.gbr, harp output expander fron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]
